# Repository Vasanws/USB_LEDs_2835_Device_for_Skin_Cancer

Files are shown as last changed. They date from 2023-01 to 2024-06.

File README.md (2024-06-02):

# USB LED Device for Skin Cancer  
In this project will show how to made Printed Circuit Board (PCB) for USB LED for Skin Cancer done from software design to transferring onto copper board as a prototype.

# How does USB LED for Skin Cancer works?  
The LEDs light wavelength was chosen specifically by the power of the light intensity it emits. A special cream applys on the affected area of the human skin and once the speical cream expose by the LEDs light, the special cream enter the skin and destroys the cancer cells.  

# How to do it as Prototype?  
There are many methods out there on creating PCB, for the best result is by using heat method with high temperature around 220 degree celcius. The tools can be use are iron or laminated machine (heavy duty). For this project, using laminated machine is one of the best tool to produce consistency in tranferring the circuit onto a copper board.  

# Step 1: Tools and Materials requires
Tools 
- Laminated Machine (heavy duty).
- Cutting mat.
- Cutting knife.
- Overhead projector or torchlight.
- Laser printer.
- Milling machine (drill)
- Gloves.
- Eye protection.
- Etching tray.
- Container for water.
- Container or beaker for PCB tinning.
- Hotplate.
- Kicad 6.
- Inkscape.
- Multimeter.
- Sanding machine.

Materials
- Semi-gloss paper 230gsm or lower gms.
- Etching Solution (Ferric Chloride).
- Thiourea (12.5 grams).
- Tartaric acid (8.8 grams).
- Tin(II) Chloride (1.3 grams). 
- tap water (250ml).
- Acetone.
- Sandpaper.
- Tipped marker pen.
- Aluminium foil.
- Copper board.
- Sponge.
- Soap

# Step 2: Making circuit board design 
In Kicad 6 software is where to design the circuit layout as shown below.
 

# Step 3: Toner Tranfer 
In this step will show the method how to toner transfer the circuit layout from the software onto a physical board. Firstly, printout the circuit layout onto semi gloss paper. For better result, ensure that the ink are darker black after printout and stick on the semi gloss paper and no extras ink act of debris that interfere the layout's connections. If the printout is not good, clean the roller in the printer to remove ink debris or check if enough ink. To printout duplicate circuit layout in a single paper, use Inkscape to duplicate the circuit layout as shown below:

  

Before proceed to to transfer the circuit layout on the board, the copper board surface requires to be clean from oxidation and surface debris. To do that, use sandpaper and sand the copper board surface until the surface turns into a shining copper colour. Once it is done, rinse the copper board with tap water apply soap and scrub with a sponge to ensure left no dirt on the copper board surface. Finally, apply acetone on the copper board surface and wipe with cloth or tissue. The picture below shows before and after of the copper board surface. 

Before:

 

After: 



Then, place the printed circuit layout on the surface of the copper board. Make sure that the printed circuit layout ink directly touch the copper board surface as shown below.

Before:



After:



Place the aluminium foil on the surface where the printout cricuit layout gloss paper is. After few try and error, this way allows the heat transfer across the board evenly for aa large scale printout circuit layout and also for smaller singular printout circuit layout.



Then, place the board either front or back of the laminated machine depending on the model features and feed it into the laminated machine with the maximum temperature around 200 degree celcius to 220 degree celcius repeatedly. Lowest count is 35 counts of feed. This is because the laminated machine is moving at a moderate rolling speed so it require to feed it multiple counts. To make it a single count, the motor of the laminated machine requires to be modify to the slowest rolling speed. Ensure that wear gloves to avoid skin burn during the handling.

Set laminated machine temperature to maximum as shown below:



Here is an example of a trial without the aluminium foil. In this example uses a smaller scale of a singular board as the method shares the same. 



After multiple counts the copper board being feed into the laminated machine, move the copper board away from the laminated machine and cool the copper board. After the copper board is cool off, place the copper board into a container of tap water and let the gloss paper become soft and soggy and safely to peal off for about 10 minutes to 15 minutes. To indicate when will the gloss paper to be peal off, look at the contrast of the circuit layout once it become clear to see through and the gloss paper is soggy that indicates the gloss paper can be peal off and the ink will not be remove from the copper board.

Before:



After:



Once the circuit layout can be seen under the water, peal the paper off the from the board.



As the picture above, the toner transfer is not perfect nor close to perfect as some of the tracers or component footprint did not stick on the copper board. This shows that the heat transfer across the board does not reach the same level of heat during the laminating process.

Now with the aluminium foil cover the copper board and repeat the same process here is the result. Do some inspection after the pealing the gloss paper, if there is excessive paper stuck in between the circuit layout or blocking the drilling holes, use wet cloth and gentle scrap off the excessive paper that stuck on the copper board. This will later during the etching process will be easy to etch. Tested where if the excessive paper does not remove, the board will not etch properly and may excessive etching will remove the ink.



Laslty, use a tipped marker pen or permanent marker pen to do some touch up if some of the ink does not stick on the copper board. For example highlighting tracks or empty space or component footprints.

In conclusion for Step 3, to reduce extra work from redo if the toner transfer fail, do the following:
- Clean the copper board surface with sandpaper and wash with soap and scrub with sponge.
- Cover the copper board with aluminium foil once the printed circuit layout is place on the copper board.
- During the laminating process, ensure that the copper board go through at least 40 counts consistently.
- Once done, cool the copper board and place the copper board into a container of tap water to soften the gloss paper.
- Once the printed circuit layout can be see through from the gloss paper, slowly peal the gloss paper.
- Clear away any excessive paper on the board.
- Double check if there is any missing ink on the circuit layout and touch up with a tipped marker pen.

# Step 4: Etching
Before etching, recommend to cut the copper board which contains the circuit layout only to reduce waste of copper board and easier for etching for each circuit layout. Use PCB Cutter or PCB Shear or ready cut the size of the copper board of the desire size before implementing Step 3 Toner Transfer.

Steps to do etching:
- Place the copper board into an etching tray.
- Pour an amount Ferric Chloride into the etching tray.
- Tilt the etching tray left and right or vice versa to let the acid reaction active.
- Do this for about 10 to 15 minutes or lesser depending on how strong the acid reaction is.
- Check the copper board time to time whether it is completely etch off the expose copper.
- Use glove or plactic clamp to remove the board once it is done and leaving it for too long may remove the ink protected area.
- Wash the board with tap water to remove the remaining acid on the board's surface.





Once the etching is done, use acetone with cloth or tissue to remove the ink.



Use multimeter to check each connectivity whether there any copper being etch away. This is to ensure that the board does not have any defects or fixable and reuseable before solder the components on the board. May use lights to place under the board to check the overall copper trace. For example, the board is being place under a overhead projector:



This way gives a clear view to troubleshoot the copper trace. This method only works for single-sided layout.

# Step 5: Drilling the Holes
For this step, may use a Milling Drill machine or Hand Drill. In this project for the drilling uses Milling Drill machine for better drilling accuracy by hand. Drill all the board's holes.



# Step 6: Board Shaping
In this step is more towards on shaping the board following the circuit layout design. In this project the shaping done by using a sanding machine.

Before:



After:



# Step 7: PCB Tinning
Why is PCB tinning is needed? PCB tinning protects the expose copper from being oxidation and corrosion. Tinning will prolong the copper tracers to remain in good shape and functionality in its conductivity. Without tinning, the oxidation in the copper can results in difficulties in soldering.

How to create DIY tinning?
- Get a beaker or plastic container.
- Fill in 250ml of tap water.
- Heat the water using hotplate 100 degree celcius.
- Mix the chemical as following: Thiourea = 12.5 grams, Tartaric acid = 8.8 grams, Tin(II) Chloride = 1.3 grams.
- Stir the following chemicals while heating up on the hotplate.
- To know whether the chemical is ready, visual change can be seen when the liquid turns cloudy and if the liquid surface have bubbles, remove from the hotplate.
- Dip the board into the liquid and once the copper is tinned, do the next side of the board.





Comparison between tinning copper trace and non tinning copper trace.



Finishing of tinning copper trace.



---------------------------------------------------------------------------------------------------------------------
# CHANGELOG OF THE PROTOTYPE TO FINAL CIRCUIT LAYOUT
This is a layout of a USB LEDs with SMD LED component imperial code 2835. 
This is the showcase of the finished layout.  
PCB layout version 1    


Size of the layout  
Length - 100mm  
Width - 20mm

PCB layout update version 2  
 
Changelog: 
1. Added from 28 LEDs to 32 LEDs. 
2. Reposition all LEDs from diagonal positions to horizontal positions.  
3. Moves the components more outwards nearby the edge cut to make room for the LEDs spacing.  
4. Reposition U3 to the right side of the layout. 
5. Reposition other components from diagonal positions to vertical and horizontal positions.  
6. Reduce the radius Front Courtyard for both mounting hole to 0.4mm radius.  
7. The copper filler for the LED connections are set to, Pad connections: Thermal reliefs, Thermal relief gap: 0.2mm, Thermal spoke width: 0.8mm. 
8. All resistor and capacitor have been changed from 0603 to 0402 except Rx1 from 0603 to 1206. 

PCB layout update version 3  

Changelog:  
1. Added two jumper in the layout for touch sensor. 
2. Expend the copper fill between the LEDS. 

PCB layout update version 4  

Changelog:  
1. Edit LED footprint distance between two pads = 0.61mm. 
2. Route crisscross tracer between LEDs to LED's driver.  
3. Additional tracer for 5V pass through between the LED footprint with tracer size 0.2mm.  
4. Replace R1 footprint from 0402 to 0603.  
  
Schematic diagram layout 1      
 

Circuit layout update   
     
Changelog:
1. Added copper fill zone to unconnected footprint of the inverter logic U3 (pin 1). Copper fill zone with settings zone priority level : 1, clearance : 0.2mm, Pad connections : Thermal reliefs, Thermal relief gap : 0.2mm
2. Changed the size of CX1 footprint to 0603 and value to 22uF in schematic diagram.
    
PCB layout update version 5    
   
Changelog:    
1. Custom made footprint SOD-323 for D33 based on the measurement of this model https://www.vishay.com/docs/85751/1n4148ws.pdf    
2. Rearrange the components to be closer and allow some spaces for larger components.   
3. Added copper fill 5V to fill in the empty spaces on the left side of the board.    
4. Retrace the track of the connection for cleaner connection.    
    
Schematic diagran layout 2    

Changelog:    
1. Added TVS diode conneted to C2.    
    
PCB layout update version 6   

   
Changelog:    
1. Image 1 modified the testpoint hole with overlapping square pad for soldering.   
2. Image 2 modified L1 according to the specification WHC 0630 https://offer-product.oss-cn-beijing.aliyuncs.com/product/offer/attachment/2140865164/file/subPdf_4274_10144_20210414-212909770.pdf with some adjustment length : 7.7mm, pads size y-axis : 3.5mm.    
3. Remove front solder mask at the right side of the board with together with the L1 to expand soldering of larger or smaller inductor component and expose empty area for power wires.   

PCB layout update version 7   
Changelog:    
1. Update mounting hole size from 2mm to 2.2mm.
2. Slightly move D35 closer to right side mounting hole with distance between each other 0.3mm.   
3. Fix Electrical Rules Error in schemactic symbols by creating and saving custom symbols in project.   

PCB layout update version 8   
   
   
Changelog:    
1. Cleanup copper fill to make the workspace clean.   
2. Custom resistor footprint for Rx1 combine metrics (1206/0805).

PCB layout update verion 9  
Changelog:  
1. Change R6 resistor value to 990 ohm.
2. Change C5 capacitor value to 33nF.

PCB Paneling  
PCB paneling for fabrication.  
  

Final fabrication  
  

-------------------------------------------------------------------------------------------------------------   
How to install Kikit in Kicad6 ?    
1. Open Kicad 6.0   
2. At the menu of Kicad 6.0, search **"Plugin and Content Manager"** under **tools** or can be seen from the right of the menu or **Ctrl + M**.   
3. Select **Plugins** Tab and search for **KiKit** and click install. Select **Libraies** tab and search for **KiKit Library** and click install.   
4. Click Apply Changes to proceed installation.   
5. Open pcbnew and under **Tools** search **External Plugins** and click refresh plugins.   
6. If plugins didn't shown, open **Kicad 6 Command Prompt**.    
7. In Command Prompt, enter **pip install kikit**.    
8. Once done, open pcbnew and refresh plugins.    
Installation guide can be found here: https://pypi.org/project/KiKit/

-------------------------------------------------------------------------------------------------------------
# REFERENCES
- Home-made mixture for chemical PCB tinning (acid bath) - https://robertgawron.blogspot.com/2016/04/galvanic-pcb-tinning-by-using-home-made.html
- Make Homemade PCB Tinning solution ("Liquid Tin") - https://www.reddit.com/r/electronics/comments/77tcpb/make_homemade_pcb_tinning_solution_liquid_tin/
- How to Make Double Sided Circuit Boards at Home - https://www.youtube.com/watch?v=au2ba5gWLWk

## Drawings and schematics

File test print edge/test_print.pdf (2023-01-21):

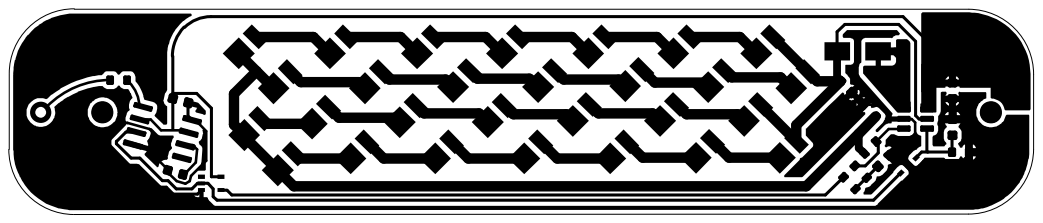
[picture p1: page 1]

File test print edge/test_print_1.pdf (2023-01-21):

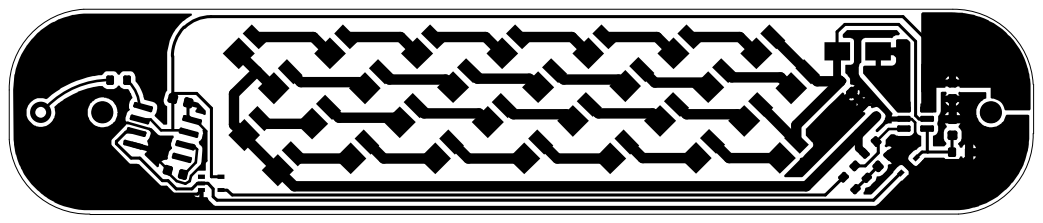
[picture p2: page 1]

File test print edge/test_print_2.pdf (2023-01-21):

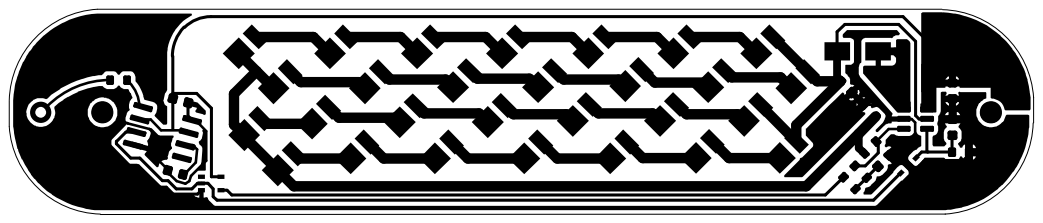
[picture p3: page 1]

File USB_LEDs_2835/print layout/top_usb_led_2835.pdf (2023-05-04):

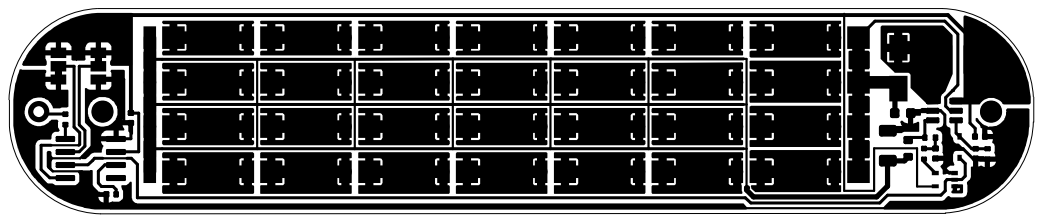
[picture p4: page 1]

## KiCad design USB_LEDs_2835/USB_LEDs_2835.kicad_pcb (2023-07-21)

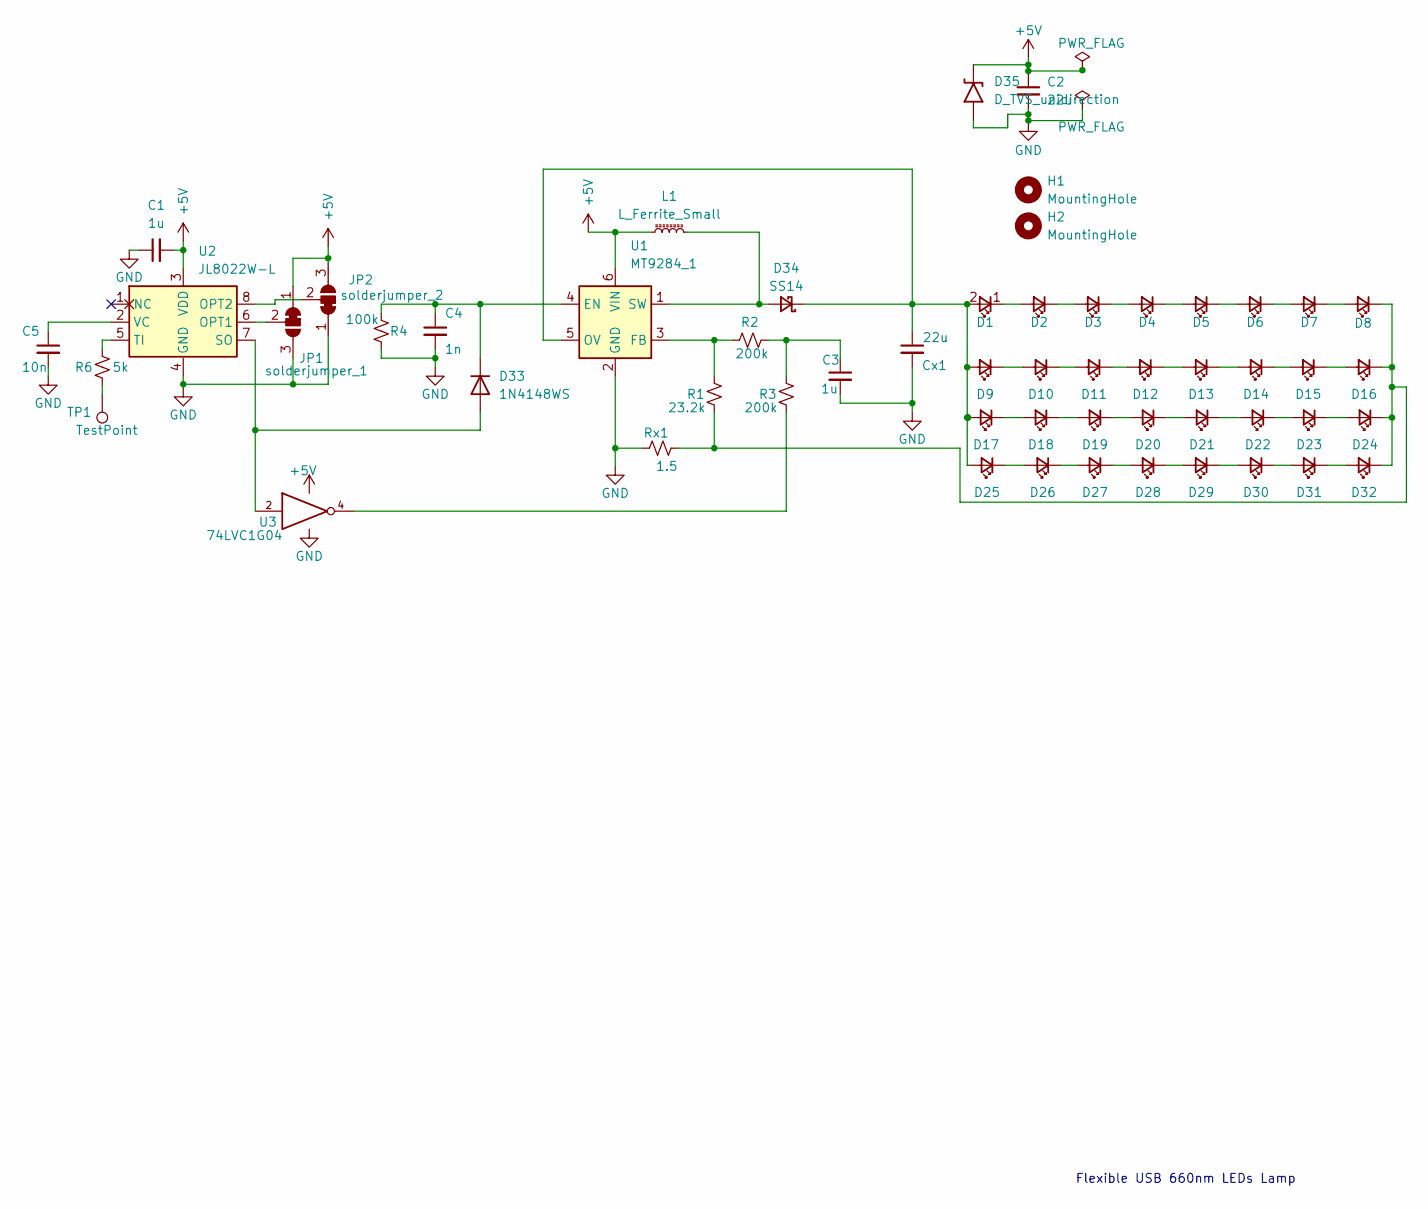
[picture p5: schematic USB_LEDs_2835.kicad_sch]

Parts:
C1, C3: 1u; C_0402_1005Metric
C2: 22u; C_0603_1608Metric
C4: 1n; C_0402_1005Metric
C5: 10n; C_0402_1005Metric
Cx1: 22u; C_0603_1608Metric
D1, D2, D3, D4, D5, D6, D7, D8, D9, D10, D11, D12, D13, D14, D15, D16, D17, D18, D19, D20, D21, D22, D23, D24, D25, D26, D27, D28, D29, D30, D31, D32: 660nm; LED_2835_custom_margin
D33: 1N4148WS; D_SOD-323_custom
D34: SS14; D_SMA
D35: D_TVS_unidirection; D_SOD-923
H1, H2: MountingHole; MountingHole_2.1mm
JP1: solderjumper_1; SolderJumper-3_P1.3mm_Bridged12_Pad1.0x1.5mm_NumberLabels
JP2: solderjumper_2; SolderJumper-3_P1.3mm_Bridged12_Pad1.0x1.5mm_NumberLabels
L1: L_Ferrite_Small; L_WHC_0630_custom
R1: 23.2k; R_0603_1608Metric
R2, R3: 200k; R_0402_1005Metric
R4: 100k; R_0402_1005Metric
R6: 5k; R_0402_1005Metric
Rx1: 1.5; R_1206_0805_3216Metric_custom
TP1: TestPoint; TestPoint_Loop_D2.50mm_Drill1.0mm_overlap_pad_custom
U1: MT9284_1; SOT-23-6
U2: JL8022W-L; SOIC-8_3.9x4.9mm_P1.27mm
U3: 74LVC1G04; SOT-353_SC-70-5

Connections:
+5V: C1.2, C2.1, D35.1 (A1), JP1.1 (A), JP2.3 (B), L1.1, U1.6 (VIN), U2.3 (VDD), U3.5 (VCC)
GND: C1.1, C2.2, C3.2, C4.2, C5.2, Cx1.2, D35.2 (A2), JP1.3 (B), JP2.1 (A), R4.1, Rx1.1, U1.2 (GND), U2.4 (GND), U3.3 (GND)
unnamed: C3.1, R2.2, R3.2
unnamed: C4.1, D33.1 (K), R4.2, U1.4 (EN)
unnamed: C5.1, U2.2 (VC)
unnamed: Cx1.1, D1.2 (A), D9.2 (A), D17.2 (A), D25.2 (A), D34.1 (K), U1.5 (OV)
unnamed: D1.1 (K), D2.2 (A)
unnamed: D2.1 (K), D3.2 (A)
unnamed: D3.1 (K), D4.2 (A)
unnamed: D4.1 (K), D5.2 (A)
unnamed: D5.1 (K), D6.2 (A)
unnamed: D6.1 (K), D7.2 (A)
unnamed: D7.1 (K), D8.2 (A)
unnamed: D10.1 (K), D11.2 (A)
unnamed: D9.1 (K), D10.2 (A)
unnamed: D11.1 (K), D12.2 (A)
unnamed: D12.1 (K), D13.2 (A)
unnamed: D13.1 (K), D14.2 (A)
unnamed: D14.1 (K), D15.2 (A)
unnamed: D15.1 (K), D16.2 (A)
unnamed: D8.1 (K), D16.1 (K), D24.1 (K), D32.1 (K), R1.1, Rx1.2
unnamed: D17.1 (K), D18.2 (A)
unnamed: D18.1 (K), D19.2 (A)
unnamed: D19.1 (K), D20.2 (A)
unnamed: D20.1 (K), D21.2 (A)
unnamed: D21.1 (K), D22.2 (A)
unnamed: D22.1 (K), D23.2 (A)
unnamed: D23.1 (K), D24.2 (A)
unnamed: D25.1 (K), D26.2 (A)
unnamed: D26.1 (K), D27.2 (A)
unnamed: D27.1 (K), D28.2 (A)
unnamed: D28.1 (K), D29.2 (A)
unnamed: D29.1 (K), D30.2 (A)
unnamed: D30.1 (K), D31.2 (A)
unnamed: D31.1 (K), D32.2 (A)
unnamed: D33.2 (A), U2.7 (SO), U3.2
unnamed: D34.2 (A), L1.2, U1.1 (SW)
unnamed: JP1.2 (C), U2.6 (OPT1)
unnamed: JP2.2 (C), U2.8 (OPT2)
unnamed: R1.2, R2.1, U1.3 (FB)
unnamed: R3.1, U3.4
unnamed: R6.1, TP1.1
unnamed: R6.2, U2.5 (TI)

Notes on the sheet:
Flexible USB 660nm LEDs Lamp

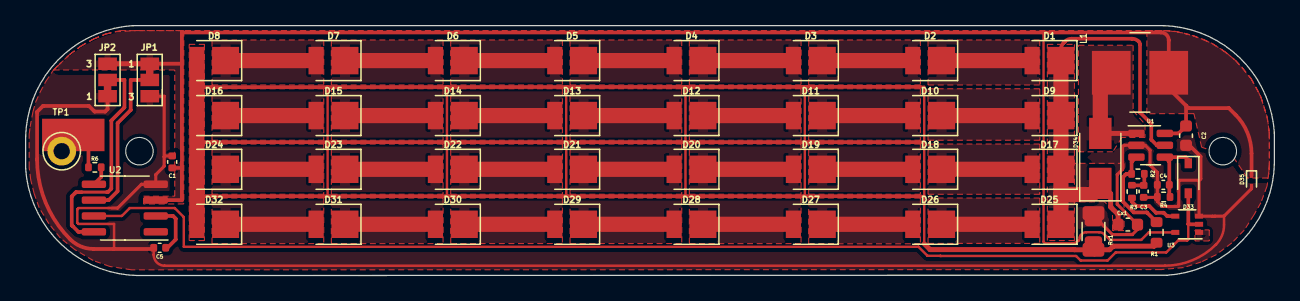
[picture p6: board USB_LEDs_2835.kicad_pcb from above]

Board: 2 copper layers, 99.9 x 20.0 mm, 56 parts (0 on the bottom side), 43 nets.
